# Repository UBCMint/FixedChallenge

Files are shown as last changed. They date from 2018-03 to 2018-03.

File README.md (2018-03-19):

# Mentha 1.0

### Background

For the NeurotechX competition Fixed Challenge, MINT is building an EEG collection system from scratch, that will accurately and effectively collect scalp potentials and minimise noise.
The system will use an Arudino microcontroller to send the data aqcuired to the computer. We will then use a python script to live-plot the fourier transform of the data recieved. 

We made our design choices based on availability and affordabiliity such that other teams can recreate our system. 

### Usage
This four channel EEG collection system can be easily set up and used. The scripts can be downloaded from the github repository and can be run with any Python interpreter. The four electrodes should be clipped onto the hair and placed closely against the scalp. Alternatively, gel electrodes can be placed on the forehead. 
The four electrode signals will be processed through the circuit and received by the Arduino Leo pins A0-A3. The 4 signals will be fourier transformed and displayed on the computer through a python plotting script. 

**Important**: Remember to change the port name to what you see in your Arduino IDE (e.g. "Arduino Leonardo on COM4") and to run the correct Arduino program for whichever script you're using (2Reads for 2Time2FFT.py, 4Reads for 4Time.py and 4FFT.py)

## Mechanical:
We used CAD to design the case for the electrical components out of 3D-printed ABS and sheet metal, with the goals of minmizing interference between the parts and keeping the assembly as small as possible. 

We also designed many different styles of electrodes for the EEG system. Choosing to 3D-print the electrodes and then coat them in conductive silver paint allowed us to fully optimize their geometry for skin contact through hair.

## Electrical:
The 4-channel EEG system consists of a notch filter, voltage regulator, and instrumentation amplifier. 

INA114 Instrumentation Amplifier Circuit

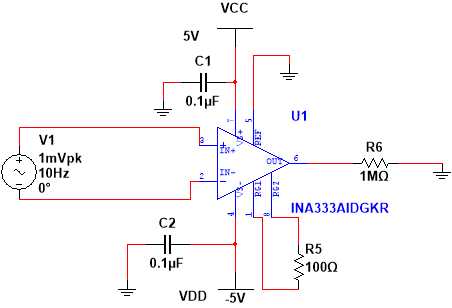
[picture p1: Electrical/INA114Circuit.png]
INA114 Circuit


The INA114 circuit acts as a differential amplifier -- it takes an EEG signal from the head and amplifies the difference between it and a reference signal. By implementing four of these circuits, we are able to achieve four EEG channels. Since the Arduino can only read from 0 to 5 volts, the signal acquired through the electrode is amplified by a INA114 precision instrumentation amplifier from microvolts to volts. The INA114 was chosen because it was readily available and affordable. 

Shifter Circuit

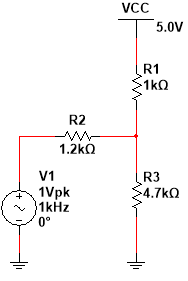
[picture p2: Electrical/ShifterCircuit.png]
Shifter Circuit


The shifter circuit takes the output of the INA circuit, which is in the range of -5V to +5V, and alters it to make it compatible as an input to the Arduino. The shifter reduces the amplitude of the signal by a half and shifts it to be in the range of 0V to +5V, as required by the Arduino. 

Notch Filter

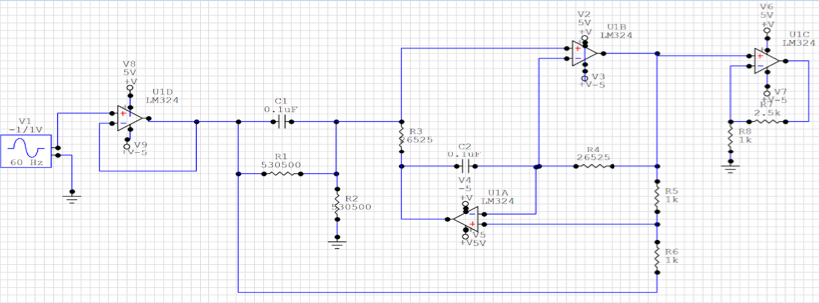
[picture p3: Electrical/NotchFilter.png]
Notch Filter


The notch filter then filters out 60Hz noise that arises from power line interference using the LM324 quadruple operational amplifier. Lastly, the 9V battery connects to a voltage regulator to power the entire circuit.

### Limitations

A limitation of Mentha's electrical system is the amount of space available within the mechanical chassis, as we wanted to keep the device small and portable. We had to design our circuits wisely to have efficient use of the available space. In the future we would implement our design on a PCB to optimize layout and increase reliability. 

## Software:
We are using python to collect data from an Arduino and plotting the fourier transform of the the EEG signal in realtime. This allows us to see the peaks in amplitude of the different frequencies of brain signals.

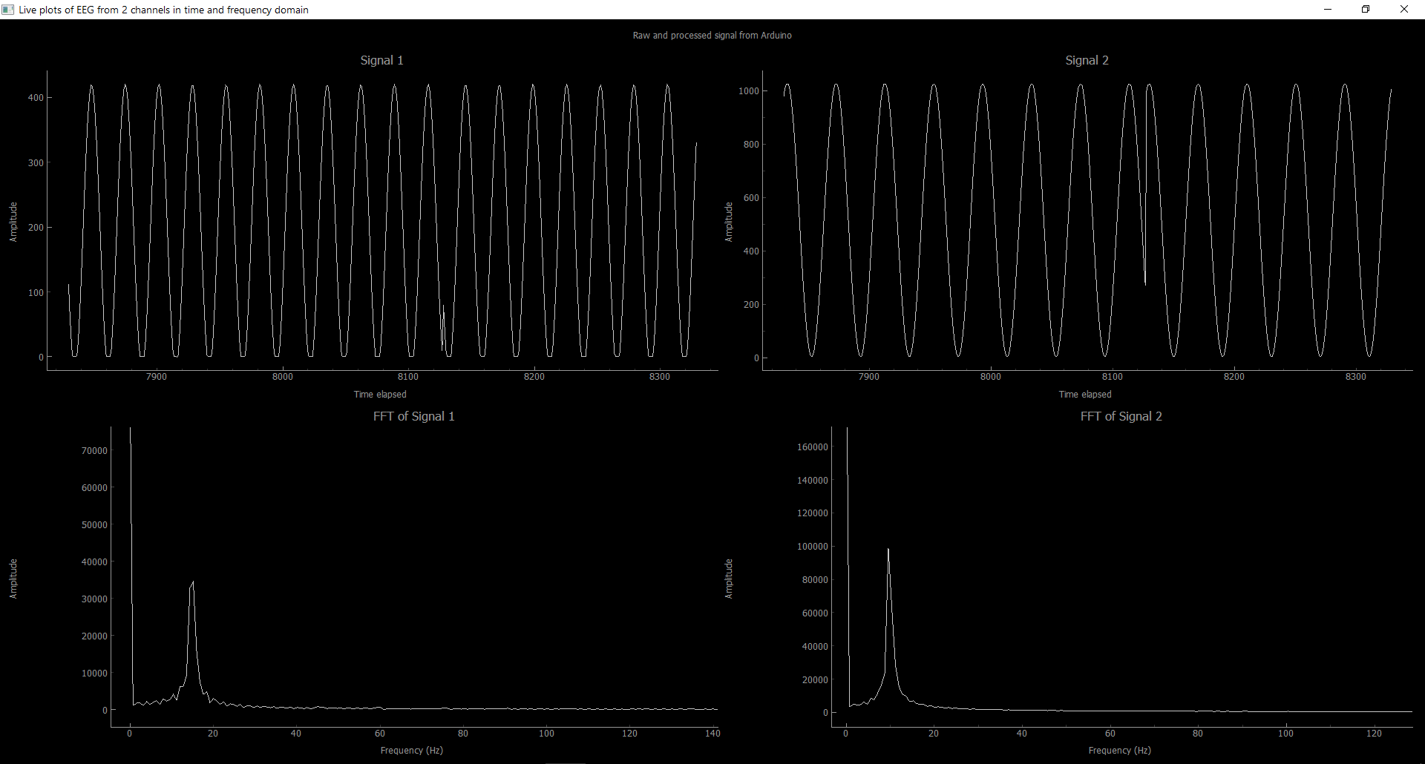
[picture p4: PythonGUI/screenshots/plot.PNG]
Python GUI


We chose to use pyqtgraph instead of matplotlib to improve the speed of live plotting. We originally prototyped with Matlab, but found that Python provided a better GUI and realtime plotting.
As seen in the above figure, the top two graphs depict the original sine wave and the bottom two graphs depict the transformed graph. The script can be easily changed to display 4 FFT plots from 4 channels.

Some challenges we had in designing this script was sending the signals through the serial port and making sure python was able to designate the right label to each signal. For example, when a signal from a single channel was missed such as A1, the remaining signals would shift and the previous
A2 would become A1. This was solved by sending all four signals in a string from the Arduino and then parsing in Python accordingly. 

### Limitations
The limitations of the software application include the number of channels that acquire data and the delay in the real-time plotting.

To increase the number of channels, we could use more of the pins available on the Arduino. This can be easily added into the python script, albeit we are limited to the 
number of pins on the Arduino or microcontroller we are using. In the future, we could add more interative components to our system, such as a GUI that allows the user to start and stop data acquisition. Another improvement would include the ability to save data and retrieve previous data. These
extra features could also be implemented through a phone app.

## Budget

Below is the rough breakdown of costs, for those who want to replicate this design:

INA114 x4	= $16  

LM7805 x2	= $4  

Standard resistors/capacitors =	~$2  

LM324 x4 = $2  

Sheet aluminium (4 sq. ft. estimate) = $30  

Protoype boards x2 = $14 

Wires	(as needed) = $10  

3D Printing Filament (30g @ $0.02/g) = $0.6  

Nuts and Bolts = $20  

TOTAL	$98.6  return

## About Us

Mentha was created by the [(Medical Innovation in NeuroTechnology](https://ubcmint.github.io/) (MINT) team of undergraduate students, part of the group [Biomedical Engineering Student Team](http://www.ubcbest.com/) at the University of British Columbia in Vancouver, Canada.

Mentha was submitted as a project for the Fixed Challenge category of the [NeuroTechX 2018 Student Club competition](https://neurotechx.github.io/studentclubs/competition/).

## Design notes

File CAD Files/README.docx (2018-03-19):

***Enclosed are the files for the mechanical components of our project. You’ll find scale models of the filter circuits and the Arduino Leo (see full assembly file for general placement), as well as the 3D-printed central shelf and battery holder, and the sheet metal case. For convenience, we have included STL and Solidworks files of all the case components. 3D-printable electrode files can be found in the STL file.

Metal Case: The metal case acts as a Faraday’s Cage, protecting the internal electrical components from unwanted electromagnetic fields. The metal case is made out of thin aluminum metal sheets and assembled using Epoxy Glue and tape to form the rectangular shape. The following dimensions were used to construct the metal case, such that they would fit the 3D printed shelf:

- Height: 36mm - 38mm
- Width: 66mm - 68mm
- Length: 135mm - 138mm

Electrodes: We decided to 3D print our electrodes using PLA plastic and coated them with conductive silver paint (Hisco Brand, 45% Purity) because this method was quick, cheap and allowed our team to iterate upon designs. The data sheet for the silver paint we used can be found here: https://www.electrolube.com/core/components/products/tds/044/SCP.pdf This idea was inspired by the following article: www.mdpi.com/1424-8220/16/10/1635/pdf

The following types of electrodes were constructed for this project:

A) Concave Electrodes:

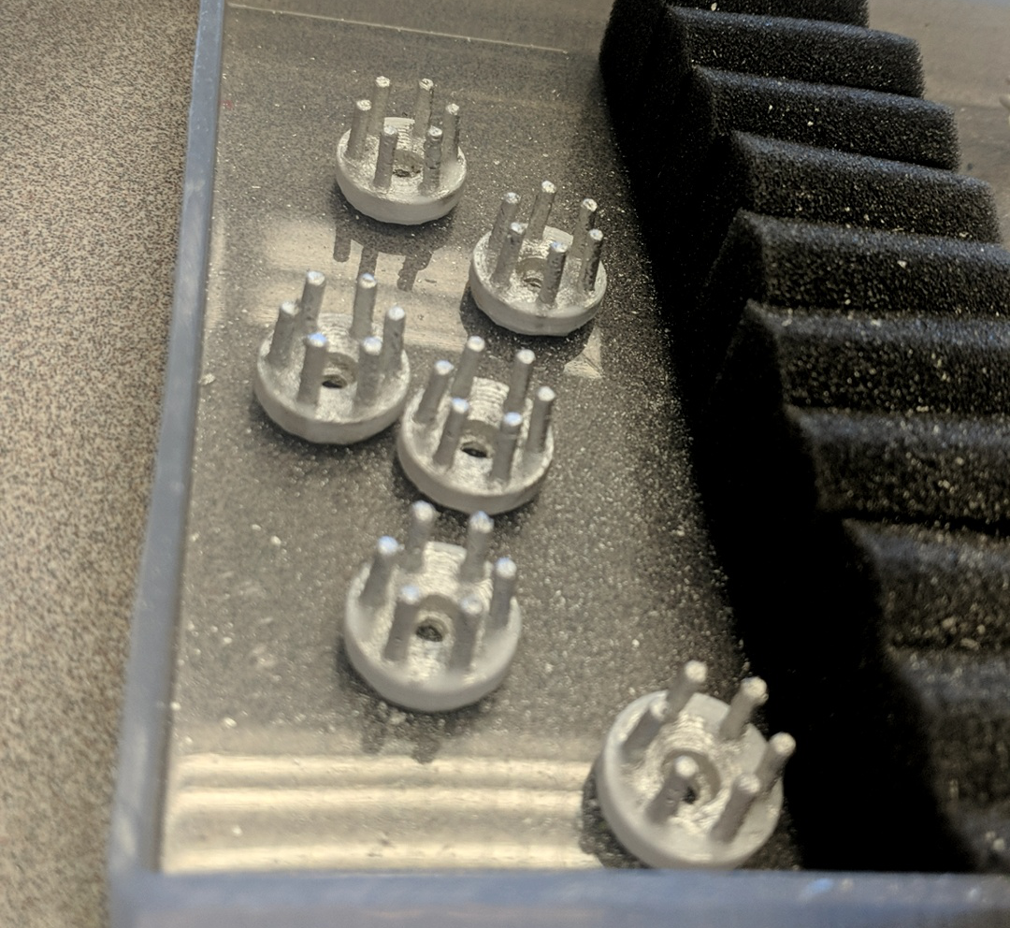
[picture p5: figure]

These electrodes were designed to contain ‘spikes’ that penetrate through the hair and maximize contact area with the scalp. The dimensions of the electrodes can be found on the STL and Solidworks files. They have screw holes that allow them to be secured to any sort of hair band, headset or holder.

B) Hair Clip Electrodes:

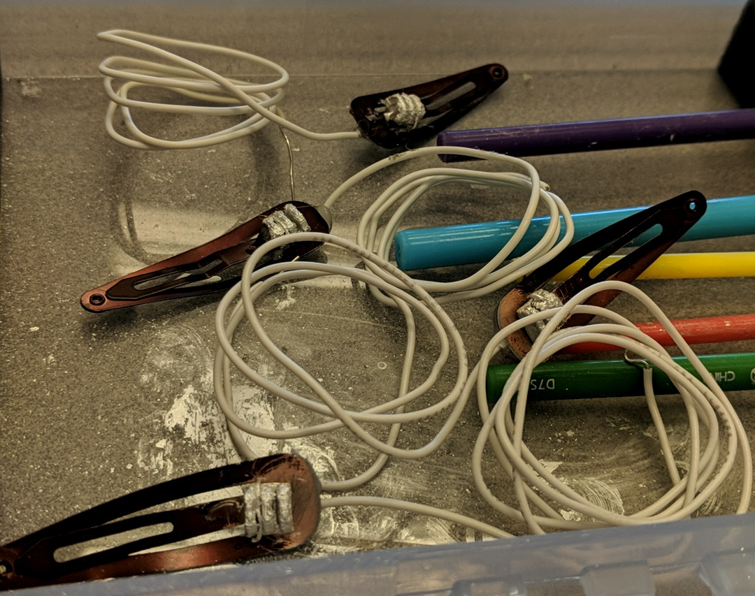
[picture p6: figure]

The hairpin electrodes were square-shaped, containing ridges that can penetrate through ize contact area with the scalp. Once printed, they can be painted with silver paint like the concave electrodes and then secured to any standard hair clips, such as barrettes, using hot glue. This facilitates attachment to hair while maintaining adequate scalp contact. The design of these electrodes were inspired by the following article: http://ieeexplore.ieee.org/stamp/stamp.jsp?tp=&arnumber=7300517&tag=1

Battery Holder:

Our battery holder was designed to give us approximately -5V to +5V, so batteries should be loaded into it as seen below. We set “ground” to be on the shelf (left) using some wire and rubber.

Above, you can see how we set up each terminal of our battery. We used four standard 3V CR1130 Lithium Ion batteries, but their output current turned out to be insufficient to sustain both boards, so this aspect of the design is not to be replicated. The dimensions of the battery holder may be easily altered in any CAD program to fit other batteries and deliver adequate current (~50mA).

Central Shelf

This shelf was designed to keep components separate and organized, with notches for the battery holder, screw holes for the circuit boards, and room for zip ties. You can see the fully assembled battery holder on the left, as well as an STL file of the full assembly enclosed.

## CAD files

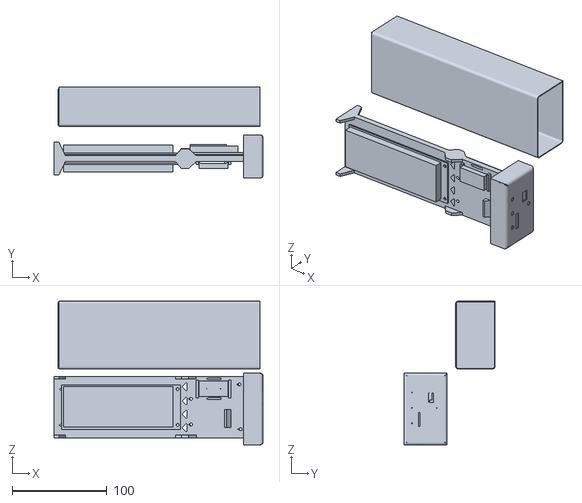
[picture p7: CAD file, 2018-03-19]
CAD Files/STL (electrodes included)/Case/Full Assembly.stl
220.4 x 96.1 x 151.5

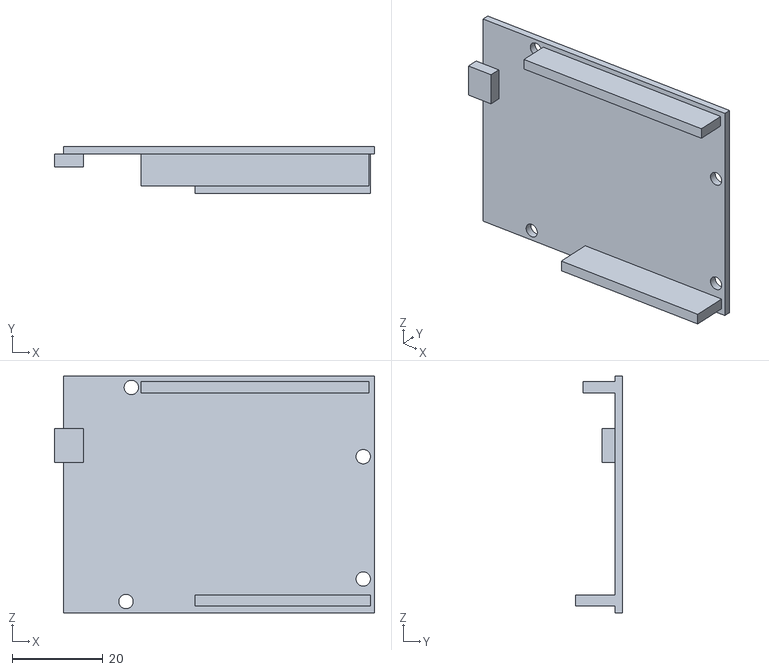
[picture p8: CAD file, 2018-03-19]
CAD Files/STL (electrodes included)/Case/Individual Parts/Leo Arduino Board.stl
70.7 x 10.4 x 52.3

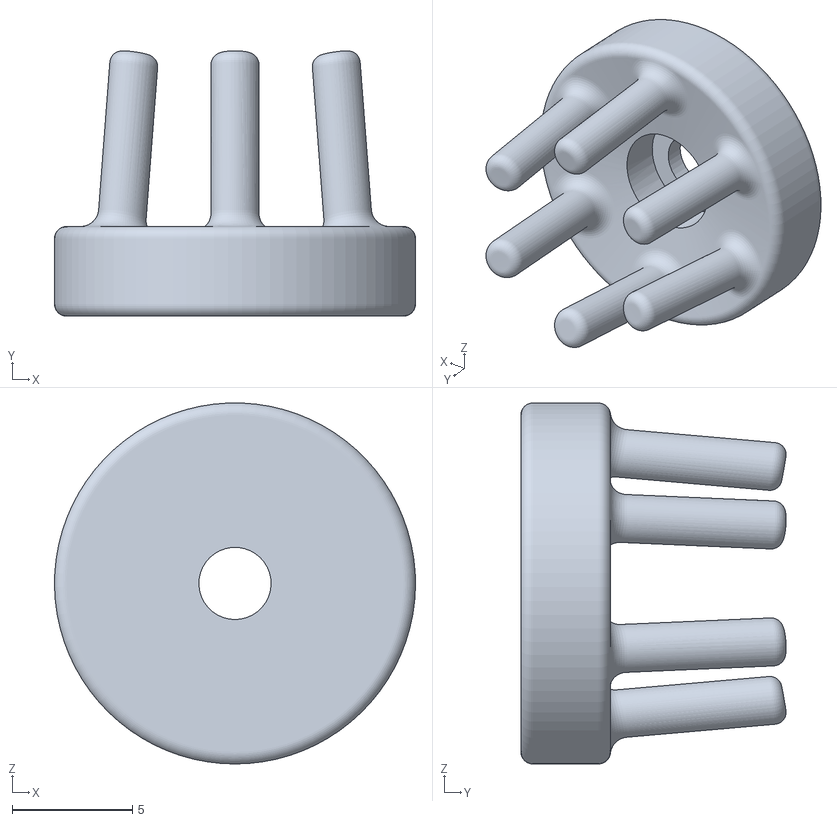
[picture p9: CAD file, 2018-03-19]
CAD Files/STL (electrodes included)/Electrodes/Concave.STL
15.0 x 11.0 x 15.0

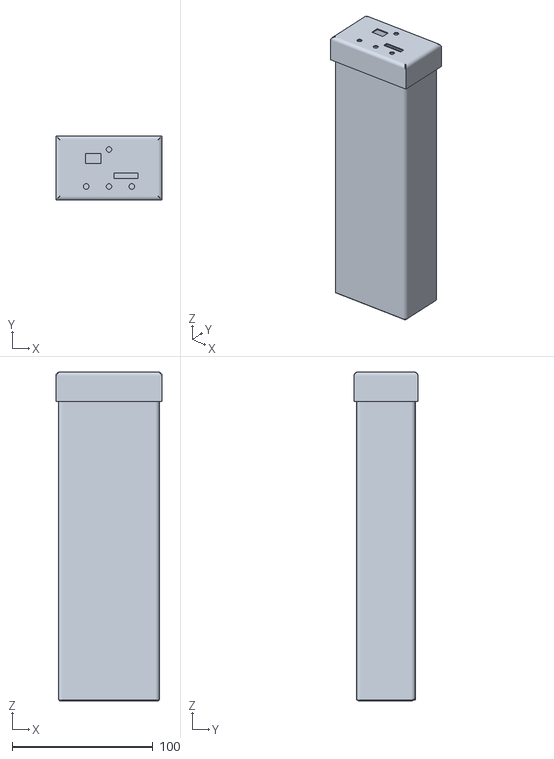
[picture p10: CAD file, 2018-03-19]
CAD Files/STL (electrodes included)/Case/Individual Parts/Metal case.stl
75.6 x 45.6 x 233.6

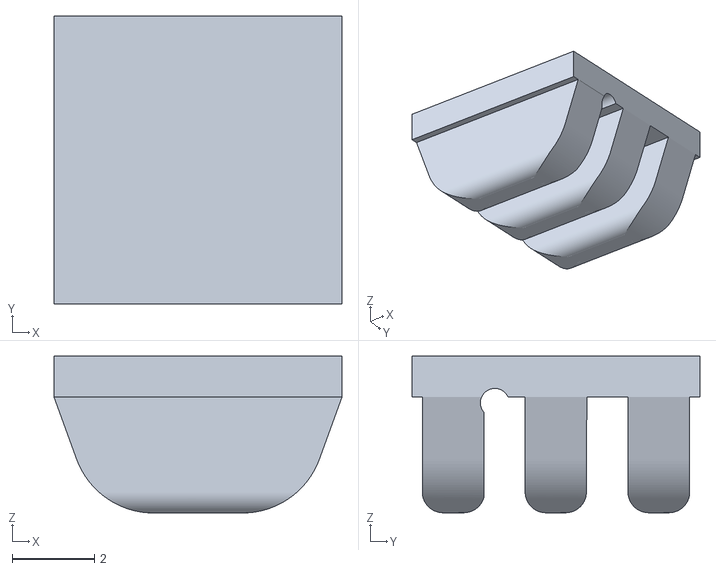
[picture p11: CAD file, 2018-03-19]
CAD Files/STL (electrodes included)/Electrodes/Hairclip.stl
7.00 x 7.00 x 3.82

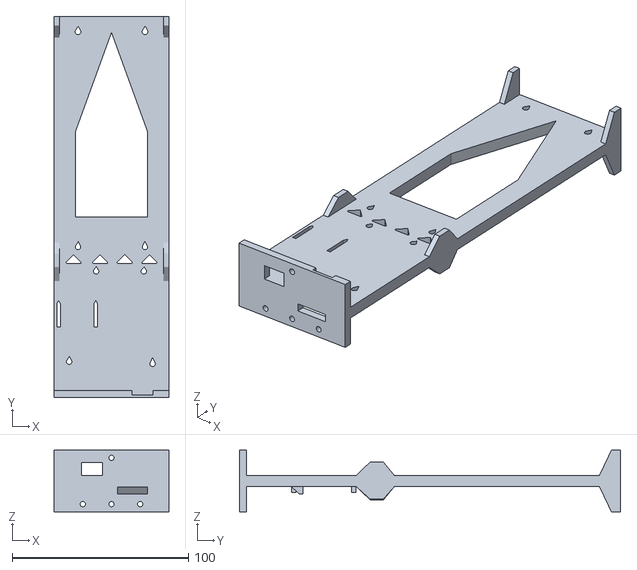
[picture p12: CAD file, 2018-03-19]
CAD Files/STL (electrodes included)/Case/Individual Parts/Central Shelf.stl
65.0 x 216.0 x 35.0

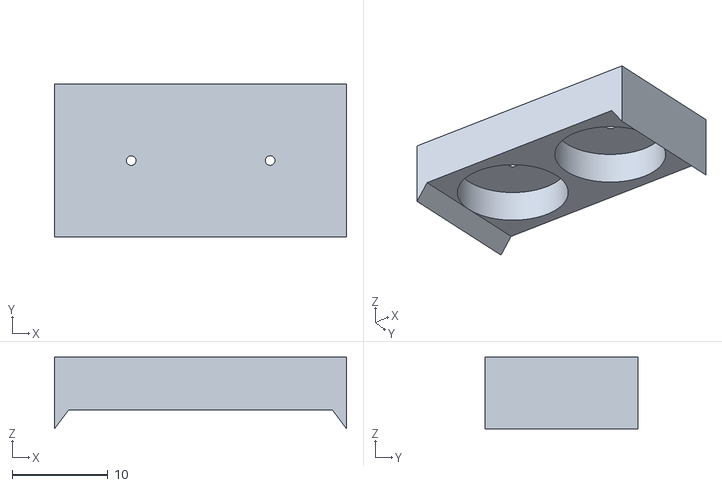
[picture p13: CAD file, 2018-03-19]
CAD Files/STL (electrodes included)/Case/Individual Parts/Battery Holder.stl
30.5 x 16.0 x 7.50

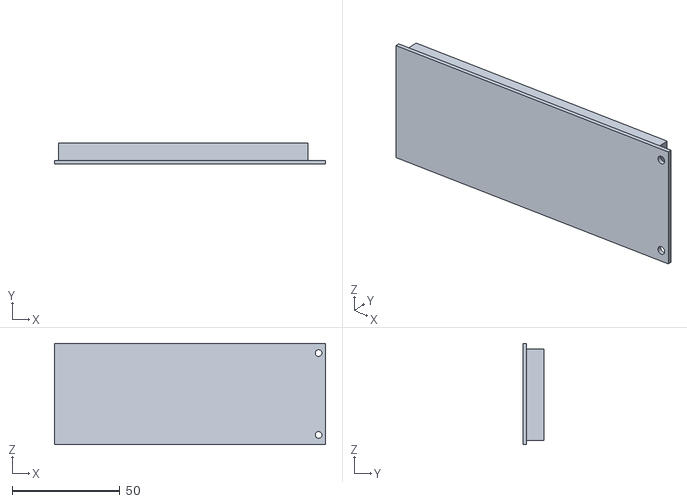
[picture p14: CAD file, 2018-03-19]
CAD Files/STL (electrodes included)/Case/Individual Parts/Filter Circuits.stl
125.6 x 9.60 x 47.0

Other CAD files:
CAD Files/Solidworks (electrodes not included)/Filter Circuits.sldprt
CAD Files/Solidworks (electrodes not included)/Leo Arduino Board.sldprt
CAD Files/Solidworks (electrodes not included)/Metal case.sldprt
CAD Files/Solidworks (electrodes not included)/Central Shelf.sldprt
CAD Files/Solidworks (electrodes not included)/Battery Holder.sldprt

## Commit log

2018-01-19 Plot arduino dummy data in matlab and save to txt file with timestamp
2018-02-03 Fixed real time plot and voltage readings and increased baud rate
2018-02-03 Added fft subplot and added buffering to increase sample rate
2018-02-10 Modified buffering rate and added sample data
2018-03-07 did some good stuff - plotted serial data from arduino
2018-03-14 plots 4 graphs from data from 4 pins on arduino
2018-03-18 added notch filter diagram
